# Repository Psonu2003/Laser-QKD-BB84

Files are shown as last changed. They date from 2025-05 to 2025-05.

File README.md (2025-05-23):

# Laser-QKD-BB84

This repository houses the code used for the physical QKD BB84 apparatus (as mentioned in [**Laser_QKD**](Supplementary_Information/Laser_QKD.pdf)). The code consists of Arduino Uno code for laser control and measurement as well as the Control Center code for the webpage and Python backend. Further instructions and descriptions will be discussed below.

## Code Compatability

The code in this repository was developed with consideration of using an Arduino Uno. The Arduino code considers the wiring as shown below.

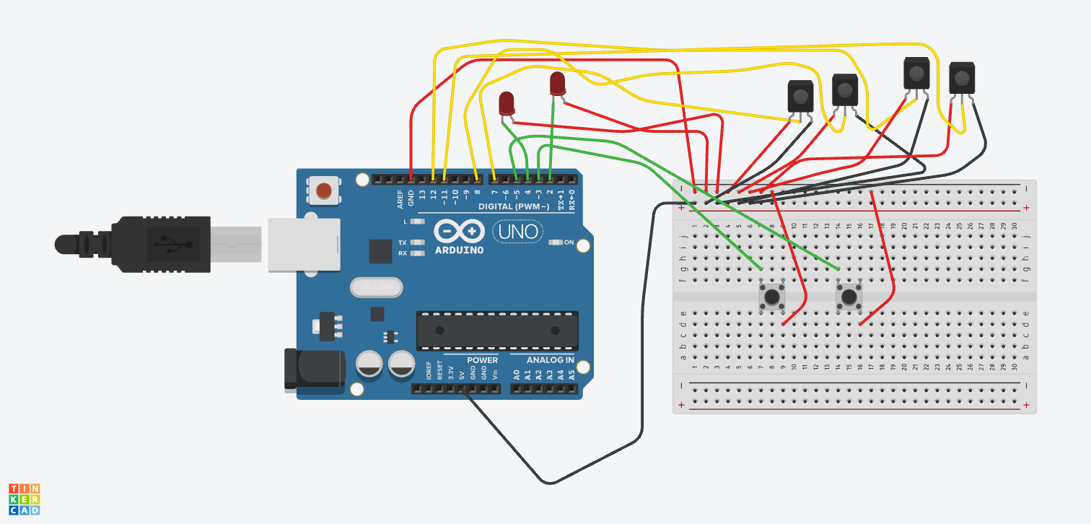
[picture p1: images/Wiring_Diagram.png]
Wiring_Diagram


In the wiring above, the red LEDs represent the 2 KY-008 laser modules and the IR receivers represent the 4 laser reciever sensor modules. The two buttons on the breadboard are optional and can be used for calibrating the apparatus.

For the control center webpage, Python and Node.js are required.

## Setup

Once the basic wiring setup (as shown in the wiring diagram above) is complete, upload the [`QKD_Control2.ino`](QKD_Code/QKD_Control2.ino) onto the Arduino Uno. Do this **after** calibration is complete (discussed in the next section). On the Arduino software, take note of the port. The port will be listed as `/dev/cu.usbmodemXXXX` where the `XXXX` are numbers. Thsi port can be found when selecting the Arduino Uno device near the top left of the Arduino application or at the bottom right after selection. Edit the `PORT` variable in the [`main.py`](QKD_Code/qkd-frontend/main.py) under the `Serial Setup` comment. An important note is to keep the Arduino Uno plugged into the **same** USB port on the computer or else the `PORT` address will change and the prior steps need to be repeated.

During protocol operation, the Arduino Uno must stay plugged into the computer. Before anything, first install [Node.js](https://nodejs.org). After the code is uploaded onto the Arduino, open Terminal or Command Prompt in the directory where `requirements.txt` is located. In the repo, it's in `QKD_Code > qkd-frontend > requirements.txt`. Then, do the following command in the current directory

``` bash
# It will be helpful to keep the venv name 'qkd_venv'
python -m venv qkd_venv
```

For Windows Command Prompt,

```bash
qkd_venv\Scripts\activate.bat
```

For Mac/Linux,

```bash
source qkd_venv/bin/activate
```

Next do,

```bash
# Install Python libraries
pip install -r requirements.txt

# Install required dependencies for React+Vite. Requires Node.js
npm install
```

Now that the environment is setup, run `run.py` using

```bash
python run.py
```

This should automatically run both the Python backend and React+Vite frontend in two different terminal windows. If there are no errors, look for the window that says `VITE` and `Local`. Copy the localhost address and paste it into the browser. This is the control center webpage. Now, run the protocol as desired.

## Calibration

To calibrate the optical setup described in the [**Laser_QKD**](Supplementary_Information/Laser_QKD.pdf)) paper, upload [`QKD_Control.ino`](QKD_Code/QKD_Control.ino) to the Arduino instead of [`QKD_Control2.ino`](QKD_Code/QKD_Control2.ino). This code utilizes the two buttons wired earlier in the wiring diagram. Each button activates one of the two phases of the protocol. The serial output can be read out with a small Python script.

```py
import serial
import tkinter as tk
from threading import Thread
import json
prev_data = ""
ser = serial.Serial('/dev/cu.usbmodemXXXX', 9600) # 9600 is the Serial baud rate. Make sure this matches the Arduino baud rate.
ser.reset_input_buffer()  # flush any unread junk
while True:
    line = ser.readline().decode().strip()
    try:
        data = json.loads(line)
        # print(data["Name"], data["Bit"])
        print(data.get("Name"), data.get("Bit"))
        print(data)
    except json.JSONDecodeError:
        print("Invalid JSON:", line)
```

Use this to see if the detectors are properly measuring results in each phase. 

## Control Center Webpage Guide

The webpage allows users to activate a phase in the QKD BB84 protocol. The top panel includes three subpanels detailing information on **Alice**, **Eve**, and **Bob**. At the start, only **Alice** should have a single number (just under her name). If anyone else has numbers right at the start, please hit **Restart** below. The number under **Alice's** name is the first bit she wants to send to **Bob**. At the bottom of her panel, it will indicate how many bits **Alice** will send in total. This number can be changed at the bottom in the **Bit Input** panel. The bits are limited to 1. Hit `Enter` or `Return` to finalize the change while in the input box. 

Underneath **Alice's** bits, the basis for the current bit is listed. This will be the encoding basis for the current bit. Similarly, the measurement bases for the current bit are listed in **Eve's** and **Bob's** panels. Set the physical apparatus accordingly. Complete the phases until there are no more bits left to transmit. After transmission is complete, the `Analysis` button will be available to see the channel security. 

### Contact

For further information or assistance, please reach me at [pratham.gujar30@gmail.com](mailto:pratham.gujar30@gmail.com).

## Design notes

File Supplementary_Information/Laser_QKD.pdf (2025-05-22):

# Laser QKD BB84 Protocol

Pratham Gujar

May 2025

## 1 Abstract

This report presents a classical optical implementation of the Quantum Key Distribution (QKD) BB84 protocol using laser modules, polarizing optical components, and Arduino-based control logic. The BB84 protocol, developed by Bennett and Brassard, enables two parties to securely exchange encryption keys while detecting potential eavesdroppers by utilizing principles from quantum mechanics. In this setup, laser beams are polarized with half-wave plates (HWPs) and polarizers to simulate quantum bits (qubits), and beamsplitter cubes serve as polarizing beamsplitters (PBS) for measurement. The system is calibrated to distinguish between horizontal/vertical (H/V) and diagonal/antidiagonal (D/A) polarizations, offering a clear and hands-on illustration of the protocol. While this demonstration uses classical light rather than single photons, it still captures essential features such as basis mismatches and eavesdropper detection. The setup performed reliably under ambient lighting, although issues such as polarizer nonuniformity and stray light are noted. Suggested improvements include adding additional HWPs for easier basis switching and testing longer bit sequences to evaluate detection accuracy. This implementation provides a practical and educational method for exploring quantum cryptography without requiring quantum hardware.

## 2 Introduction

Quantum computing has been presented with the promise of solving several computationally heavy problems. These include complex simulations for fusion reactors, materials science, and drug development. Other problems include traffic analysis and machine learning. However, the focus here will be on cryptography. Quantum cryptography seeks to implement new methods utilizing the natural, occurring, and immutable laws of quantum mechanics [1]. Despite being a new concept, this technology has the potential to be significantly more secure than classical protocols and may theoretically be unhackable. It is also capable of breaking modern-day encryption methods such as RSA using Shor’s algorithm. These advancements, however, will take time to develop due to hardware limitations. Advanced quantum algorithms require stable qubits and

1

increased scalability. This report will focus on a simpler encryption protocol that can be demonstrated classically using lasers: the Quantum Key Distribution BB84 protocol.
The Quantum Key Distribution (QKD) is the most common type of quantum cryptography, theorized by Charles Bennet and Gilles Brassard in 1984 [1]. This protocol was designed to exchange a secure key between two parties by collaboratively constructing a shared private key. These secured keys can be used for classical symmetric key encryption methods. These methods use a secure key to both encrypt and decrypt data. Examples include Vigen´ere and Caesar encryption methods. These methods are much simpler and easier to break compared to asymmetric methods such as RSA encryption since the hacker only needs to obtain the secure key.
They can do this by intercepting it through a communication channel or by analyzing the encrypted key for patterns. Assuming the hacker knows how the two parties will communicate their shared private key, the hacker will pick the easier approach to intercept the key. For the convention, Alice will generate the secure key and send it to Bob. Eve will be the eavesdropper and will attempt to steal the key. Eve wants to remain undetected because she will need Alice and Bob to think that nobody stole their shared private key so that they will use their key to encrypt and decrypt sensitive data. So, Eve needs to ensure Bob receives the secure key that Alice generates. Alice’s key, no matter what she chooses, will be serialized into a bit string so she can send it to Bob digitally. If Alice transmits her key classically, Eve can capture and copy each bit and then send the copied bit to Bob. Classical bits do not decohere, thus allowing for nearly perfect cloning for each bit. So, classically implementing this would be advantageous to Eve since Alice and Bob will not know if their key has been stolen until their encrypted data is leaked. However, quantum mechanics changes the tide to the advantage of Alice and Bob.

## 3 QKD BB84 Protocol

Drawing on the laws of quantum mechanics, Alice and Bob are now able to detect with high probability if someone is intercepting their shared secret key. The QKD protocol allows Alice to encode her secure key into photons and transmit them to Bob who then measures the photons [1]. The photons are called quantum bits or ”qubits”. They differ from classical bits since photons, depending on environmental interferences and measurement devices, decohere. So, if Eve measures the photons Alice sent, there is a 50% chance Eve will measure the correct bit and will transmit the correctly encoded photon to Bob. The 50% comes from how Alice prepares her photon and how Eve measures the photon. Suppose Alice can pick between two different transmission bases. Considering she is using photons, she will determine these two bases to be polarization bases: horizontal/vertical (H/V) and diagonal/diagonal (D/A) bases. Using the convention, H, D → 0 and V, A → 1, Alice will prepare her photon according to her transmission basis.

2

Suppose Alice’s key is n bits long, for each i-th bit, she will randomly select a transmission basis for each. For simplifying notation, she decides to use + for H/V and × for D/A [2]. So a sample bit string for n = 3 might be 001 and her transmission basis string will be + × +. Then, she will prepare her photons as HDV where the left-most photon corresponds to the left-most bit in the string. If Eve wants to intercept the bit, she will need to measure each photon. For simplicity, assume Alice announces she will send n bits so that both Eve and Bob know. Eve and Bob will randomly generate a measurement basis for each photon. Since there are only two possible bases, Eve and Bob each have a 50% chance of picking the same basis Alice used to encode her photon.
Using their selected bases, Eve and Bob will use a polarizing beamsplitter cube (PBS) to measure the photon. The PBS cube splits light into two different paths based on their polarizations (See Figure 1). If Eve uses a PBS in the H/V basis and a H photon enters the cube, then the photon will only pass through the H side of the cube (consider this to be the P-polarization in the figure below). Similarly, if the photon was in the V polarization, then the photon would only come through the S-polarization side of the cube. However, what if Alice prepared her photon in the D/A basis but Eve measured in the H/V basis?

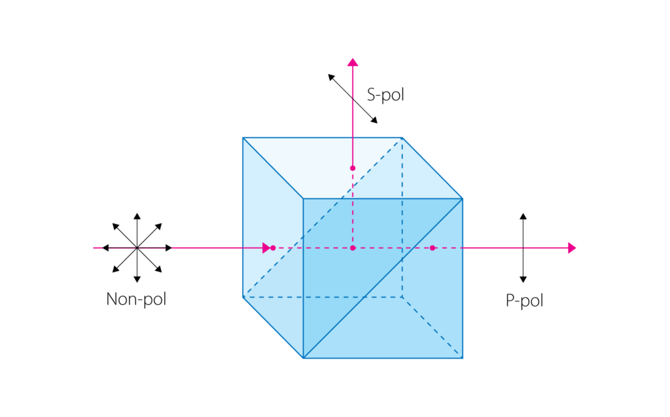
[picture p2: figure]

Figure 1: Diagram of PBS splitting non-polarized light into S-polarized and P-polarized light [3]. The S and P polarizations could be H or V in the H/V basis or vice versa in the D/A basis.

If Alice sent a D or A polarized photon, then Eve would see the photon come from the P or S polarization sides with 50% probability. This is because both the D and A polarizations have components of H and V. The D polarization is the

3

linear combination of H and V components. So, there are equal components of H and V which causes the 50% chance of the photon coming from either side. If Alice used a polarized laser beam instead of a photon, the results would average and cause Eve to see the laser beam split and emerge from both sides simultaneously. The resulting intensities would be halved.

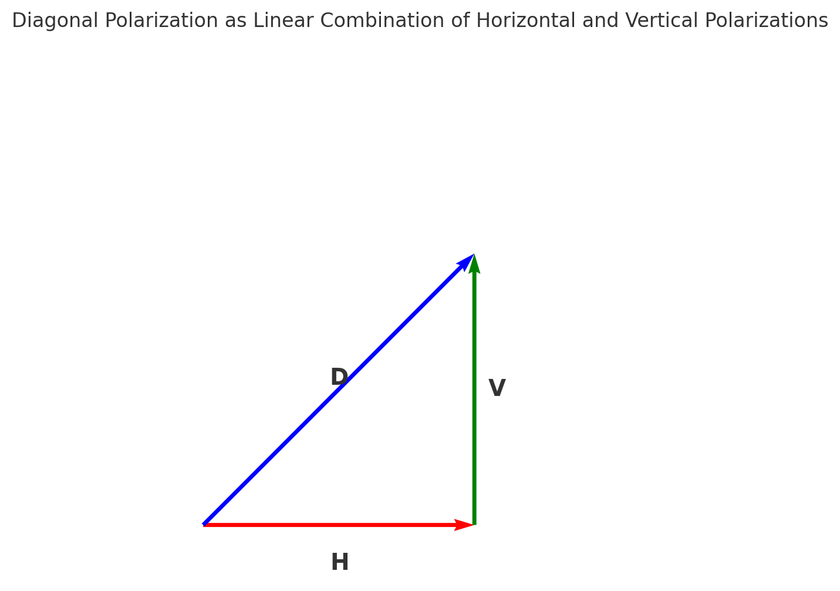
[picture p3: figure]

Figure 2: D polarization represented as the linear combination of H and V polarization vectors. The same happens with A polarization with V going the opposite direction.

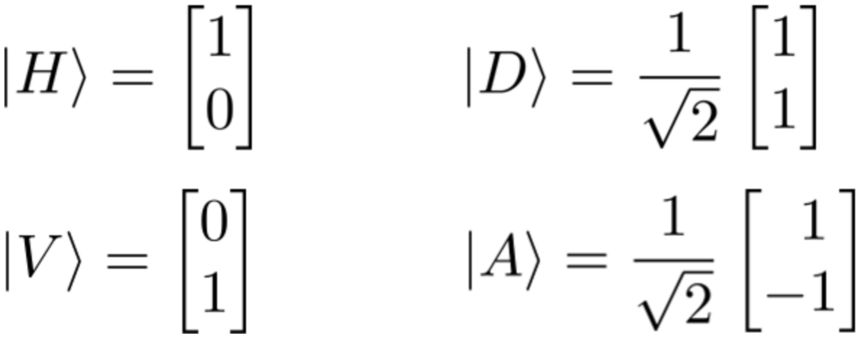
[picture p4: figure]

Figure 3: All four polarizations are represented as vectors (taken from the poster).

4

After the photon emerges, Eve will count it using a photon detector. Based on which photon detector registered a count, Eve will assume the polarization Alice prepared and then send her prepared photon to Bob. So, if Alice sent a D photon and Eve measured H in the H/V basis, then Eve will send a H photon to Bob thinking that is what Alice sent. Bob will measure with his own PBS configured to his chosen measurement basis and then record his result. So, if Alice and Bob picked the right basis for the current bit but Bob measured a different bit than what Alice transmitted, then Alice and Bob can suspect that someone, Eve, intercepted Alice’s photon but measured it on the wrong basis. Thus, Eve measured the wrong bit or measured the correct bit and prepared it on the wrong basis causing the mismatch between Alice and Bob.
This is what allows Alice and Bob to detect eavesdroppers in their communication channel. Now, in the case of photons, there are chances of decoherence due to environmental factors or false counts from the dark count probabilities of their photon detectors. This arises from the quantum nature of the photons and can still cause mismatches between Alice and Bob if they selected the same basis and there was no eavesdropper. So, Alice and Bob establish a Quantum Bit Error Rate (QBER) that accounts for this and serves as the threshold as to when a channel is no longer secure. This decoherence also fully prevents Eve from perfectly cloning Alice’s photon.
After Alice transmits all n bits to Bob, Alice and Bob will sample some number of their bits [2]. Consider they sample the first 10% of their bits. They will publicly announce what bases they selected for each of those sampled bits. Alice and Bob will then sift their sampled bases to find which bases matched for which bits. They will denote the discarded bases with a −. They will then reveal the associated bits they have for the matching bases. Alice and Bob compare their bits and count the number of discrepancies. They use the discrepancies to calculate the QBER and see if it exceeds their threshold. If it does, then they abort communication on this channel and find a different way. This highlights the entire QKD BB84 protocol. There are other QKD protocols such as B92, E91, and COW but these will not be discussed.
The implemented QKD BB84 protocol discussed in this report utilizes lasers instead of photons. So, the quantum behavior of the photon decoherence vanishes due to the averaging of the photons in the laser beam. This demonstration aims to show the essence of the BB84 protocol without quantum fluctuations in the measurements. With this implementation, one can clearly and visually see how Alice transmits her bits to Bob and how Eve attempts to steal each bit and go unnoticed.

5

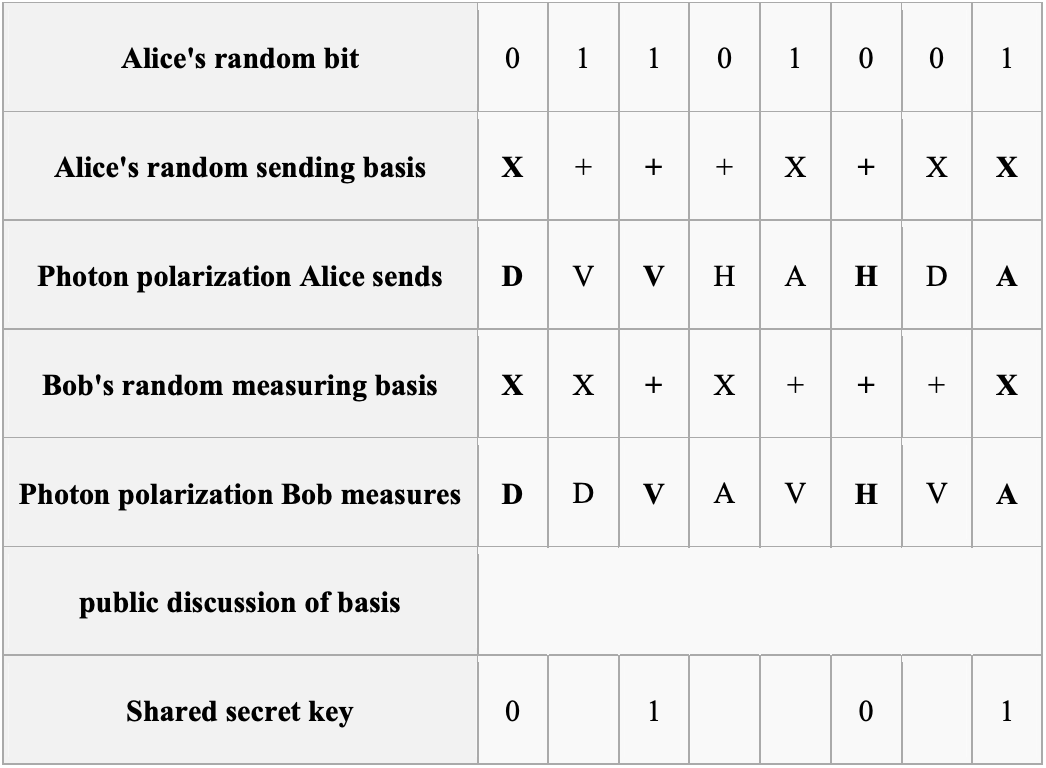
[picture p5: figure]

Figure 4: Example of a sampled bit string and bases [2]. If their QBER is under their threshold, then Alice and Bob will use their generated shared secret key for symmetric key encryption protocols.

## 4 Materials

- 2 KY-008 laser modules (630 nm)
- 4 Laser receiver sensor modules
- 2 25 mm Beamsplitter cubes
- Polarizers
- 2 25 mm Half-wave plates (HWP) [4]
- Arduino Uno
- Arduino Uno Power Supply Module
- 1 1’ by 2’ by 1.5” wooden board
- 4 2” by 2” by 0.5” wooden blocks

6

## 5 Methods

Using the materials above, I implemented the BB84 protocol split into two phases (See figures below).

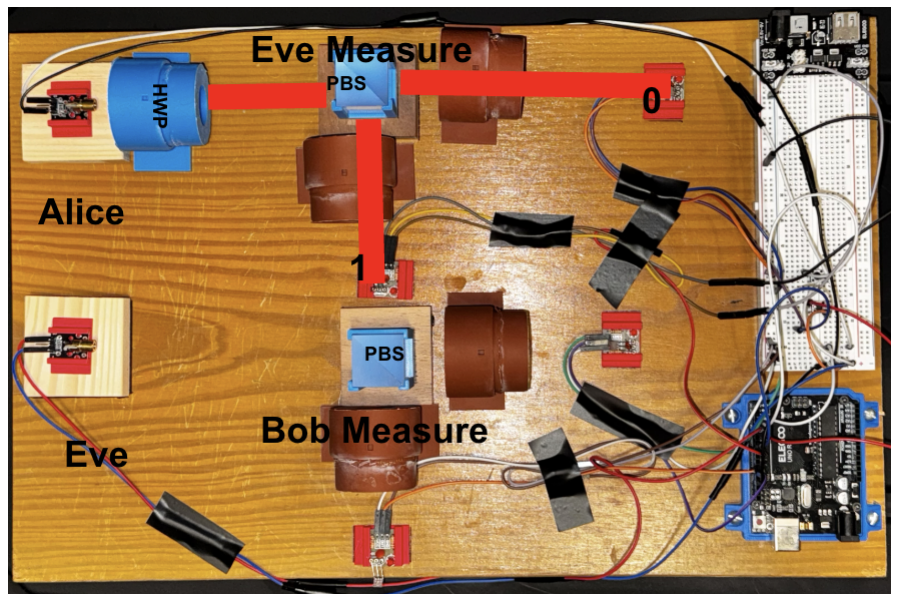
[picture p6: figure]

Figure 5: Phase 1 consists of Alice transmitting her bit to Bob and Eve intercepts this bit and measures it.

7

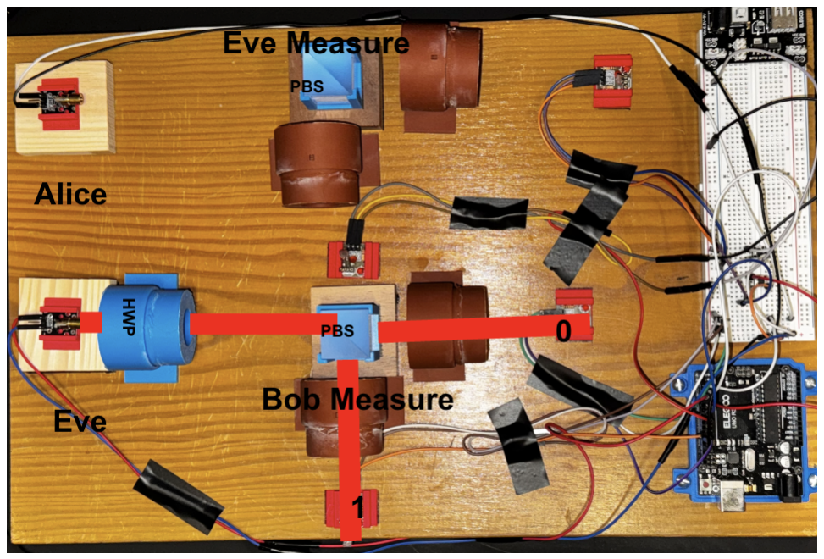
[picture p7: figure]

Figure 6: Phase 2 consists of Eve using her measured bit and chosen basis to assume what Alice sent. She then prepares the bit using her measured basis and transmits it to Bob. Bob measures the bit and records his measurement. The cycle continues until Alice has sent all of her bits.

In the figures above, the wooden blocks mentioned in Section 4, were used to mount the lasers and beamsplitters (labeled as PBS in the images). The lasers were placed into 3D printed mounts as shown in the image with the red mount base around the laser diode. The blue and brown rings (the blue one is labeled as HWP) are custom 3D-printed optical holders (my CAD files will be available on my GitHub [5]). Inside the blue optical holder is the HWP mentioned in Section 4. Inside the brown holders are cutouts of a non-adhesive polarizing film capable of filtering out H, V, D, A polarizations. The beamsplitters are inserted into another custom 3D-printed mount to prevent any scratches. The beamsplitters and polarizers combined together work as a makeshift PBS.
As for the setup and usage, the setup is quite challenging as the demonstration is sensitive to ambient light and requires much precision. The board should be arranged as it is in the images above for optimal usage. The laser must pass through the beamsplitter and the beam(s) must pass through the polarizers (brown optical holders) and must land on the detectors. Although counterintuitive, the laser beams mustn’t land on the center of the detectors (small circular section). Several factors including the ambient light and performance of the HWP and polarizers cause the detector to read false positives because of the extremely faint laser beam landing on the center. For calibration, I adjusted the laser detector instead of the laser transmitter as it allowed for much better

8

precision and accuracy.
Further calibration methods include using the Arduino buttons to activate the individual phases. The detector counts and measured bit should be analyzed to determine if calibration is complete. I followed the following steps for efficient calibration. Note that the optical holders have degree markings on them and are accurate to ±3

◦
Step 1: Set up the KY-008 laser modules (wiring discussed later) and aligned them with the laser receiver sensor modules.
Step 2: Place HWP in front of the laser for Phase 1 (Alice’s laser) and set it to 0

◦
Step 3: Set the polarizers around the beamsplitter to the H/V basis. 0◦ for the
side entering the 0 bit detector and 90◦
for the side entering the 1 bit detector (See Figure 5 for reference of the 0 and 1 bit detectors).
Step 4: Connect the buttons to the Arduino as indicated in the QKD Control.ino and also upload this program to the Arduino Uno.
Step 5: When ready, press the designated button for Phase 1 to begin the phase.
Step 6: Read the output using the Arduino Serial Monitor (or Python).
Step 7: If the measured bit is 0 and Count0 > Count1 (See Section 5.2 on how to determine this inequality), then the measurement is a success. If not, adjust the laser detector and try again.
Step 8: Repeat all previous steps but change the HWP angles for each step. HWP at 0◦ keeps the laser in the H state. At 22.5

◦
, the laser is in the D state. At 45◦
, the laser is in the V state. Lastly, at 67.5

◦
, the laser is in the A
state.
Step 9: Confirm the measurements and determine if they are as expected. Note that Count0 corresponds to the number of counts measured by the 0 detector and likewise for Count1.
Step 10: After all HWP angles are completed, return to 0◦ and then change the polarizers into the D/A basis. Both polarizers must be at 45◦
Step 11: Repeat steps 4-8.
Step 12: After Phase 1 calibration is complete, move the HWP to Eve’s laser in Phase 2 and repeat all steps but for Phase 2.
Step 13: After all calibration has been completed, upload QKD Control2.ino to the Arduino Uno and begin the demonstration.

9

### 5.1 Wiring

Properly wiring the laser components, especially the laser detector, will ensure the components remain unharmed. On the KY-008 laser transmitter, the S terminal is the voltage source terminal, the middle terminal is the output terminal, and the - terminal is the GND terminal (Refer to the datasheet [6]). The output terminal on the transmitter module outputs a voltage if the laser is supplied by power and turns on. This can be used for laser diagnostics. The transmitter should be supplied by at most 5V. Look at either QKD Control.ino or QKD Control2.ino for the S wiring. The S should be connected to an Arduino Uno numbered pin. The number of the pin is mentioned in either of the two codes mentioned earlier.
The laser detector, similar to the laser transmitter, has three pins but all three pins must be connected (See the datasheet [7]). Unlike the laser transmitter, the source pin must be connected to a steady 5V power supply. The constant 5V supply can come from the Arduino Power Supply Module (See module on the top of the breadboard in 5). The middle output pin must be connected to the Arduino numbered pins and the specific number is found in the code. The detectors associated with Eve will be mentioned as EVE DETECT0 or EVE DETECT1 (similarly for Bob). The last remaining pin should be connected to GND.
For the Arduino buttons, one pin on one side of the button (consider the left side) should be connected to its designated PIN on the Arduino as stated in only QKD Control.ino. The other pin on the right side should be connected to GND.

### 5.2 Count Similarity Threshold

The count similarity between Count0 and Count1 is determined by their ratio with the smaller quantity as the numerator. If the ratio is greater than or equal to 80%, then Count0 ≈ Count1. Now, to save on computation, it’s not necessary to know which count is the smaller quantity. For simplified notation, let Count0 be a and Count1 be b. Using the logic above,

min(a, b)
max(a, b)
≥ 0.8 ⇒ a ≈ b | (1)

To remove the logic of determining the minimum and maximum count, I rewrite Eq. 1 as

max(a, b) − min(a, b)
max(a, b)
≤ 0.2 | (2)

(3)
max(a, b) − min(a, b) = |a − b| | (4)

To simplify the denominator, I use a bounding trick.

10

max(a, b) ≥

a + b
2

(5)

(6)
1
max(a, b)

≤

2
a + b

(7)

(8)

⇒

|a − b|
max(a, b)

=

2|a − b|
a + b

(9)

Putting this into Eq. 2, this gives the final result

|a − b|
a + b
≤ 0.1 ⇒ a ≈ b | (10)

This threshold is used in the code and should also be used in the calibration steps to determine if each phase is calibrated.

## 6 Essential Optics for QKD

My implementation utilized the HWP to prepare the lasers into particular polarizations. This can be confirmed mathematically by using the Jones matrix for the HWP with θ relative to the fast-axis. The fast axis is the directional axis within the HWP medium where light travels fastest. The Jones matrix is given by
HWP(θ) =
cos(2θ) sin(2θ)
sin(2θ) − cos(2θ)

The KY-008 laser is by default in the H polarization. Using the Jones matrix for the HWP, at θ = 45◦
the calculation will yield the V vector shown in Figure 3. All angles described in the calibration steps can be confirmed mathematically using this Jones matrix applied to the H vector.

### 6.1 Demonstration Operation

Once calibration is complete, make sure that the QKD Control2.ino program is loaded onto the Arduino Uno. Then, follow the instructions on the GitHub [5] to start the QKD Control Center front end and back end. In the back end, the PORT variable in the back end should be updated to the directory listed at the bottom right of the Arduino application window when the Arduino is connected. If they do not match, the program will not work.
To run the demonstration, look at the basis in the Alice panel. Then look at the right-most bit directly above the basis. Set the HWP accordingly with this information and then look at the Eve panel. Similarly, look at the basis for the Eve panel and set Eve’s polarizers accordingly. Now Phase 1 is ready to

11 start. Activate Phase 1. After completion, use the bit Eve measured and the basis in which Eve measured to configure the HWP for Eve’s laser. Then, look in Bob’s panel and configure Bob’s polarizers according to the basis mentioned in his panel. After this is done, start Phase 2. Repeat this until Alice has no more bits to send. After all bits have been transmitted, click on Analyze at the bottom right to get the results of the demonstration.

## 7 Results And Discussion

After constructing the demonstration, the results were better than expected even in strong ambient lighting. Unfortunately, due to the nature of the demonstration, there are no figures to demonstrate the effectiveness of the demonstration. I did notice that when setting the laser polarization for Alice to A and if Eve was measuring in the H/V basis, then Eve would measure H close to 100% of the time. I determined the polarizers were not uniform and had imperfections at certain angles. If it had been uniform, then the same issue would persist for Alice transmitting the D polarization and Eve measuring in the H/V basis. Other than this, the demonstration seems to be working quite well in classroom lighting. If in the presence of sunlight or higher-intensity lights, the detectors pick up stray readings and measure incorrectly. Ultimately, this demonstration can concretely show the QKD BB84 protocol using classical optics. It demonstrates Alice and Bob’s advantage in detecting any eavesdroppers on their communication channels.

## 8 Conclusion

The demonstration successfully shows how the QKD BB84 protocol is performed between two parties and how it may be intercepted. The key result is that this implementation shows how the communicating parties can detect eavesdroppers. Some further improvements for this implementation would be to increase the number of HWPs so that the polarizer angles need not be changed but rather the HWPs for configuring the measurement bases. Another addition would be to gather test results in large bit streams (more than 20 bits) to determine how successful Alice and Bob are in detecting Eve. This would provide more concrete results on the effectiveness of this protocol. A succeeding, but significantly more advanced, demonstration can be built using photon generators and photodetectors to compare with the classical implementation of the protocol. The comparison of the results should be interesting to see how quantum effects enhance the protocol.

## 9 Acknowledgments

I would like to acknowledge Dr. Aida Torabi for her mentorship and assistance in ensuring all materials required for the apparatus were delivered on time.

12

She also greatly assisted in offering several resources to help manufacture the apparatus components such as the optical holders and laser/detector mounts. I would also like to thank Dr. Dan for his mentorship and assistance with the PMA Student Machine Shop equipment. His experience and guidance were invaluable and allowed me to precisely machine my wooden blocks for the lasers and beamsplitters. I would also like to acknowledge the CNS MakerSpace for their 3D printing training and guidance as it allowed me to create mounts for my lasers and beamsplitters as well as my optical holders. I would finally like to thank my classmates for their encouragement and peer review as their insight helped me construct my demonstration.

## References

1
IBM Quantum, Quantum cryptography, Retrieved May 2, 2025, IBM, (2023) https://www.ibm.com/think/topics/quantum-cryptography.
2M. Chekhova, Lecture 12: quantum key distribution, Retrieved May 2, 2025, Max Planck Institute for the Science of Light, (n.d.) https://mpl.mpg.de/fileadmin/user_upload/Chekhova_Research_Group/Lecture_4_12.pdf. 3Altechna, Diagram of polarizing cubes for high energy applications, Image available at: https://www.altechna.com/wp-content/uploads/2018/10/diagrama-polarizing-cubes-01-1-1024x637.png. Retrieved May 2, 2025, (2018) https://www.altechna.com/products/polarizing-cubes/polarizing-cubes-for-high-energyapplications/.
4Edmund Optics, Polymer retarder film, Retrieved May 2, 2025, (n.d.) https: //www.edmundoptics.com/f/polymer-retarder-film/14827/. 5Psonu2003, Laser-qkd-bb84, Accessed: 2025-05-02, (n.d.) https : / / github . com/Psonu2003/Laser-QKD-BB84.
6ArduinoModulesInfo, Ky-008 laser transmitter module, Accessed: 2025-05-02, (n.d.) https : / / arduinomodules . info / ky - 008 - laser - transmitter -module/.
7T. Hareendran, The mysterious laser receiver sensor module!, Accessed: 2025-05-02, (2019) https : / / www . codrey . com / electronic - circuits / the -mysterious-laser-receiver-sensor-module/.

13

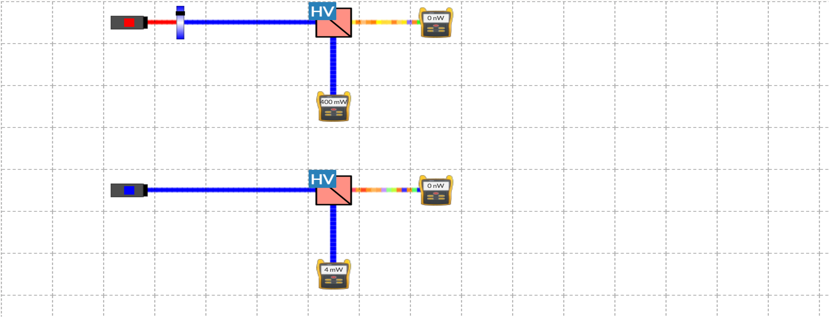
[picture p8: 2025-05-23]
images/Schematic.png

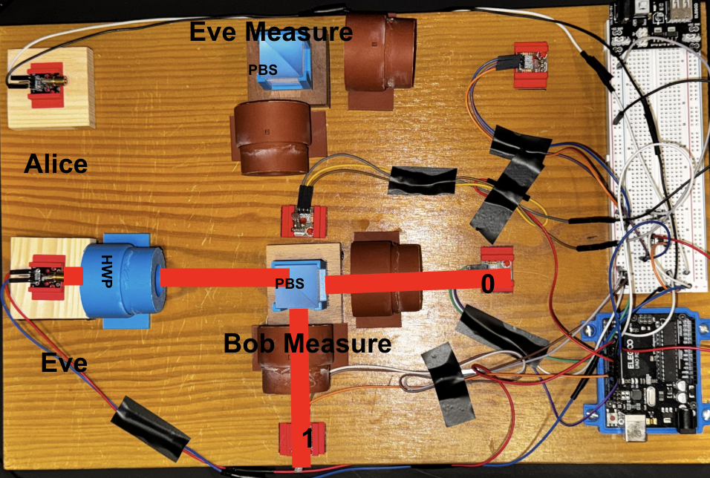
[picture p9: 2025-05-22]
images/Phase2.png

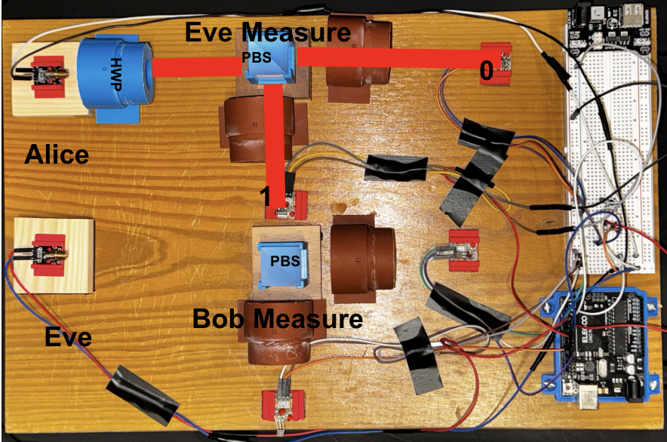
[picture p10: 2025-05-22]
images/Phase1.png

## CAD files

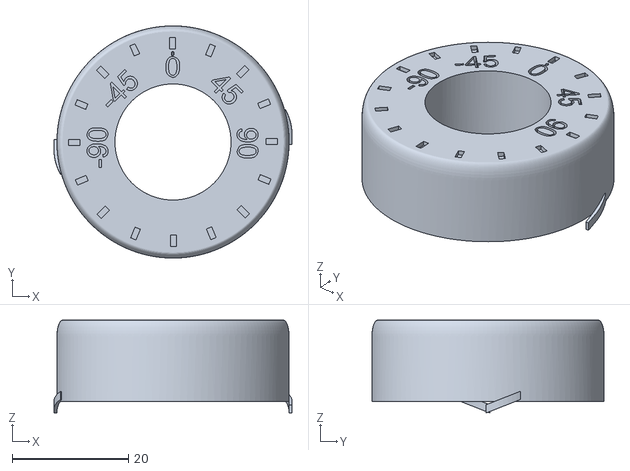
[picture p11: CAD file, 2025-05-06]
CAD_Designs/PolarizerRingTopV2.stl
41.0 x 40.0 x 16.0

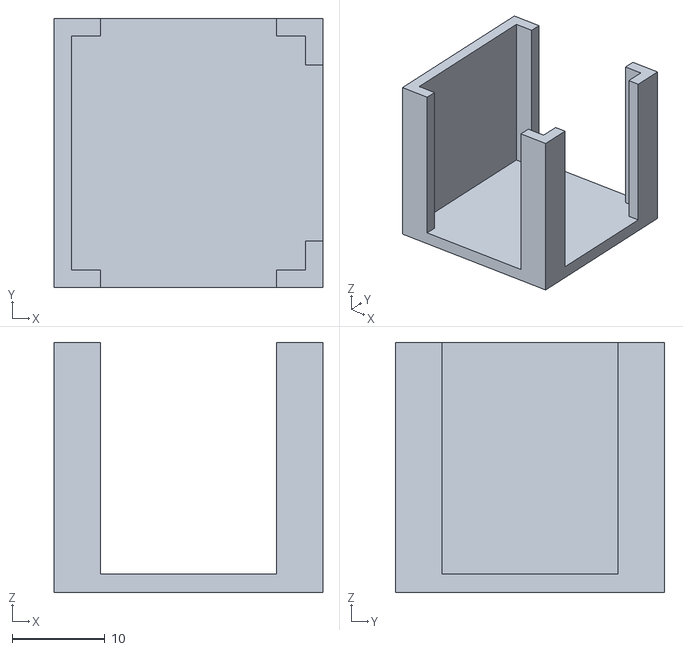
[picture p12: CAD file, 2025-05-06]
CAD_Designs/BSMount.stl
29.0 x 29.0 x 27.0

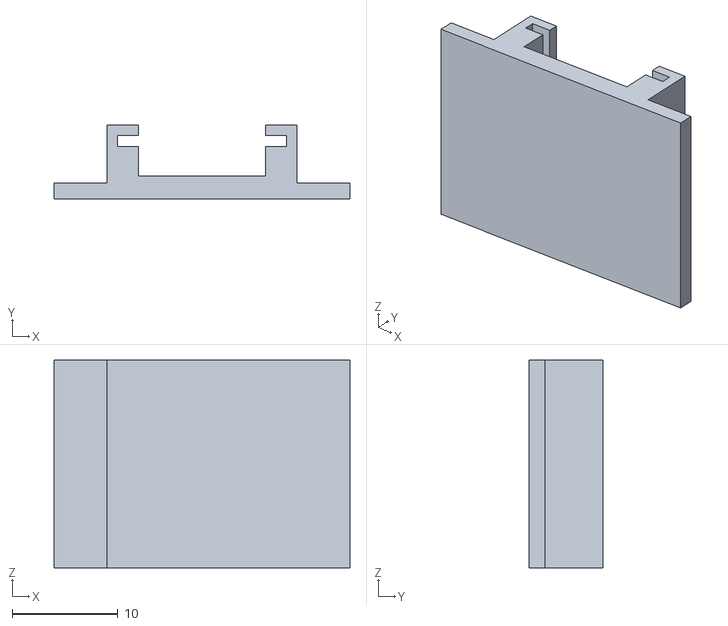
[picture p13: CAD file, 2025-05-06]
CAD_Designs/LaserMount.stl
28.0 x 7.03 x 19.7

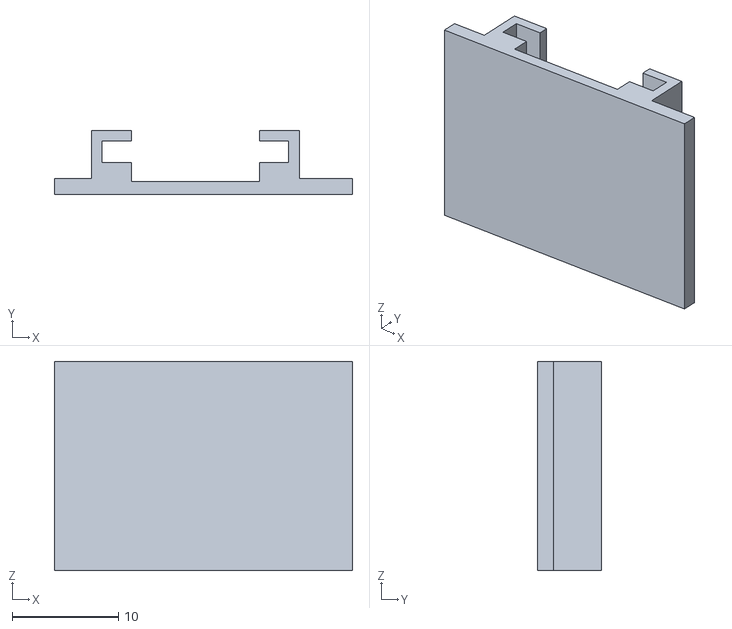
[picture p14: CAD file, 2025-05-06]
CAD_Designs/ReceiverMount.stl
28.0 x 6.00 x 19.7

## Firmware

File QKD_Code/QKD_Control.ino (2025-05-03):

#include <ArduinoJson.h>

/*
QKD BB84 Protocol Control using KY-008 Laser transmitters and Laser detectors. 
The program defines two lasers: Alice and Eve. Alice sends a bit intended for Bob but
Eve intercepts this bit and attempts to send the same bit to Bob to go undetected. 

The control protocol is divided into two phases controlled by two buttons. Button1
initiates 'phase 1' which activates Alice's laser and Eve's measurement. Button2 
initiates 'phase 2' where Eve replicates Alice's bit and Bob measures.
*/

#define ALICE_LASER 2
#define EVE_LASER 4
#define EVE_DETECT0 7
#define EVE_DETECT1 8
#define BOB_DETECT0 12
#define BOB_DETECT1 11

#define BUTTON1 3 // Phase 1
#define BUTTON2 5 // Phase 2

const float BIT_THRESHOLD = 0.025;

int detected = LOW;
int AliceState = LOW;
int EveState = LOW;
int lastButton1State = HIGH;
int lastButton2State = HIGH;

int currentButton1State;
int currentButton2State;

JsonDocument Phase1;
JsonDocument Phase2;

void setupPhaseData(){
  Phase1["Laser"] = ALICE_LASER;
  Phase1["Detect0"] = EVE_DETECT0;
  Phase1["Detect1"] = EVE_DETECT1;
  Phase1["Name"] = "Eve";

  Phase2["Laser"] = EVE_LASER;
  Phase2["Detect0"] = BOB_DETECT0;
  Phase2["Detect1"] = BOB_DETECT1;
  Phase2["Name"] = "Bob";
}


void setup() {
  // put your setup code here, to run once:
  Serial.begin(9600);

  pinMode(ALICE_LASER, OUTPUT);
  pinMode(EVE_LASER, OUTPUT);

  // turn off lasers
  digitalWrite(ALICE_LASER, LOW);
  digitalWrite(EVE_LASER, LOW);

  pinMode(BOB_DETECT0, INPUT);
  pinMode(BOB_DETECT1, INPUT);

  pinMode(EVE_DETECT0, INPUT);
  pinMode(EVE_DETECT1, INPUT);

  pinMode(BUTTON1, INPUT_PULLUP); // Phase 1
  pinMode(BUTTON2, INPUT_PULLUP); // Phase 2

  setupPhaseData();

}


void activateControlPhase(int BUTTON, int currentButtonState, int lastButtonState, JsonDocument phase){
  int LASER = phase["Laser"];
  int DETECT0 = phase["Detect0"];
  int DETECT1 =  phase["Detect1"];
  String name = phase["Name"];

  

  if (lastButtonState == HIGH && currentButtonState == LOW){ // check the falling edge of the button signal from HI to LO
    delay(50); // delay for debouncing

    if(digitalRead(BUTTON) == LOW){ // check again in case of bouncing 
      unsigned long startTime = millis();
      int count0 = 0, count1 = 0;
      JsonDocument data;
      data["Name"] = name;

      while (millis() - startTime < 2000) { // run for 2 seconds
        digitalWrite(LASER, HIGH);
        delayMicroseconds(200);

        int sample0 = 0, sample1 = 0;

        for (int i=0; i<3; i++){ // smooth our readings since detectors can be noisy
          sample0 += digitalRead(DETECT0);
          sample1 += digitalRead(DETECT1);
          delayMicroseconds(50);
          // Serial.print("Detect0:");
          // Serial.print(digitalRead(DETECT0));
          // Serial.print("  | Detect1:");
          // Serial.println(digitalRead(DETECT1));

          
        }

        digitalWrite(LASER, LOW);

        // count how many 0 or 1 bits
        if (sample0 > sample1) count0++;
        else if (sample1 > sample0) count1++;
        else if ((sample0 + sample1) > 0 && abs(sample0 - sample1) /float(sample0 + sample1) <= BIT_THRESHOLD) {
          count0++;
          count1++;
        }

        delay(10); 
        }
      int total = count0 + count1;
      if (total == 0){
        data["Bit"] = "-";
      }
      else if (abs(count0 - count1)/float(total) <= BIT_THRESHOLD) {
        data["Bit"] = random(2);
      }
      else if (count0 > count1) {
        data["Bit"] = 0;
      }
      else {
        data["Bit"] = 1;
      }

      data["Phase"] = (name == "Eve") ? 1 : 2;
      data["Count0"] = count0;
      data["Count1"] = count1;
      digitalWrite(LASER, LOW);
      serializeJson(data, Serial);
      Serial.println();
    }
  }
}

void loop() {
  // put your main code here, to run repeatedly:
  currentButton1State = digitalRead(BUTTON1);
  activateControlPhase(BUTTON1, currentButton1State, lastButton1State, Phase1);
  lastButton1State = currentButton1State;

  currentButton2State = digitalRead(BUTTON2);
  activateControlPhase(BUTTON2, currentButton2State, lastButton2State, Phase2);
  lastButton2State = currentButton2State;  
}

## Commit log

2025-05-03 Added Arduino QKD Code
2025-05-06 Added CAD designs used for project
    [BSMount.stl, LaserMount.stl, PolarizerRingTopV2.stl, ReceiverMount.stl]
